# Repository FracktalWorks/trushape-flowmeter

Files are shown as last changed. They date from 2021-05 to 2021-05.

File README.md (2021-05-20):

# Trueshape Oxymeter
An open source oxygen flowmeter alternative using CNC machining, off the shelf parts and 3D Printing to meet the demand of flowmeters in India

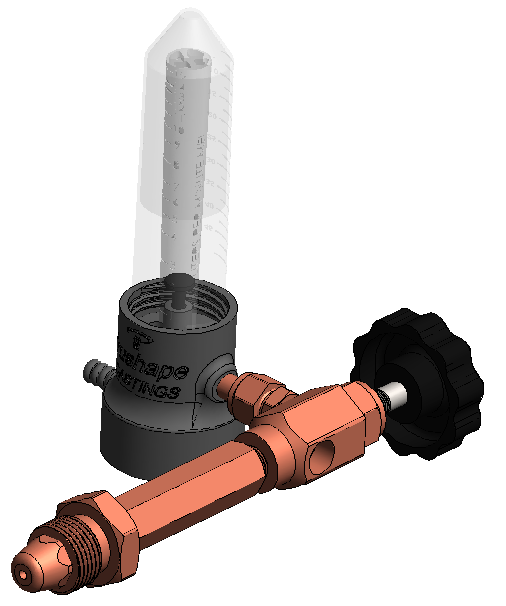
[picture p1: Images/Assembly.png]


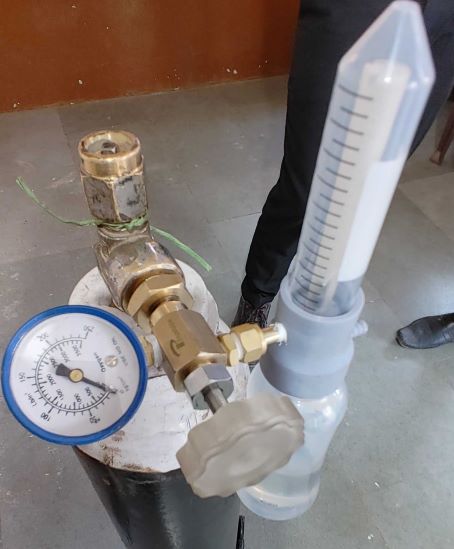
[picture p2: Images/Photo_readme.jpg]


### licence
------------------------------------------------------------------------------                                                
                                                                              
This source describes Open Hardware and is licensed under the CERN-OHL-S v2. 
                                                                              
You may redistribute and modify this source and make products using it under 
the terms of the CERN-OHL-S v2 (https://ohwr.org/cern_ohl_s_v2.txt).         
                                                                             
This source is distributed WITHOUT ANY EXPRESS OR IMPLIED WARRANTY,          
INCLUDING OF MERCHANTABILITY, SATISFACTORY QUALITY AND FITNESS FOR A         
PARTICULAR PURPOSE. Please see the CERN-OHL-S v2 for applicable conditions. 

As per CERN-OHL-S v2 section 4, should You produce hardware based on this source, You must where practicable maintain the Source Location visible      
on the external case of the Gizmo or other products you make using this
source.

------------------------------------------------------------------------------

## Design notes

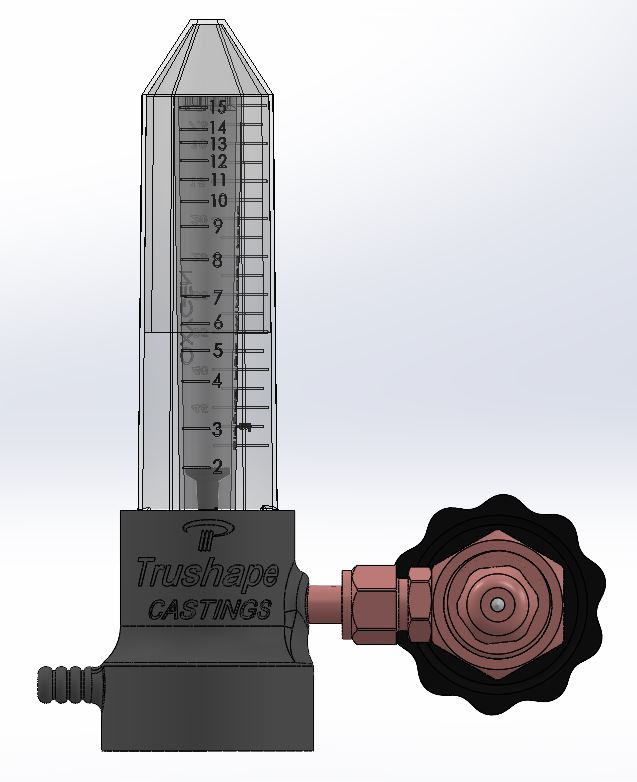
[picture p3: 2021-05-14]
Images/Front View.JPG

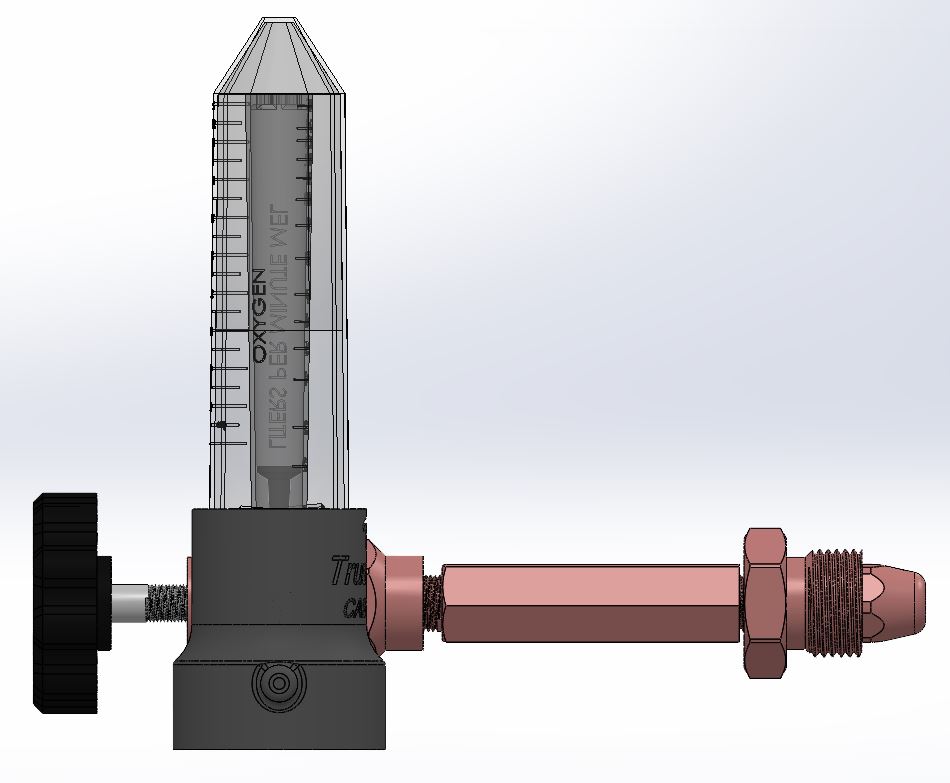
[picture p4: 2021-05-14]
Images/Side View.JPG

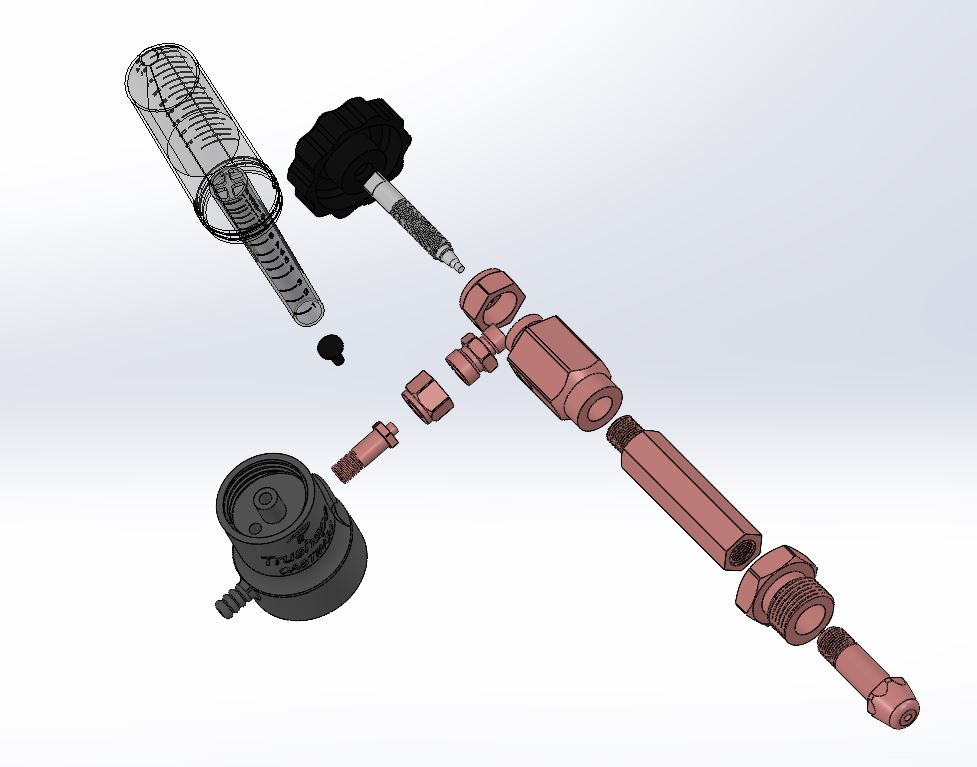
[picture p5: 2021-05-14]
Images/Exploded View.JPG

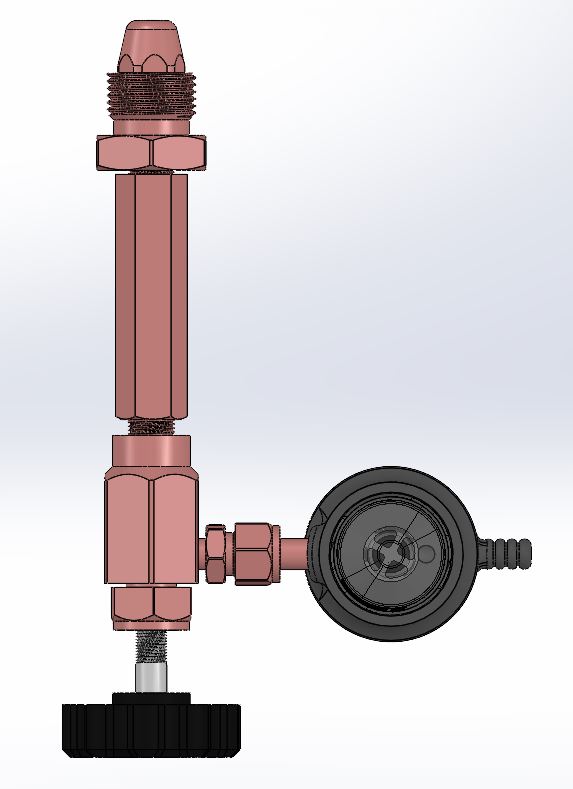
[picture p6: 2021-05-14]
Images/Top View.JPG

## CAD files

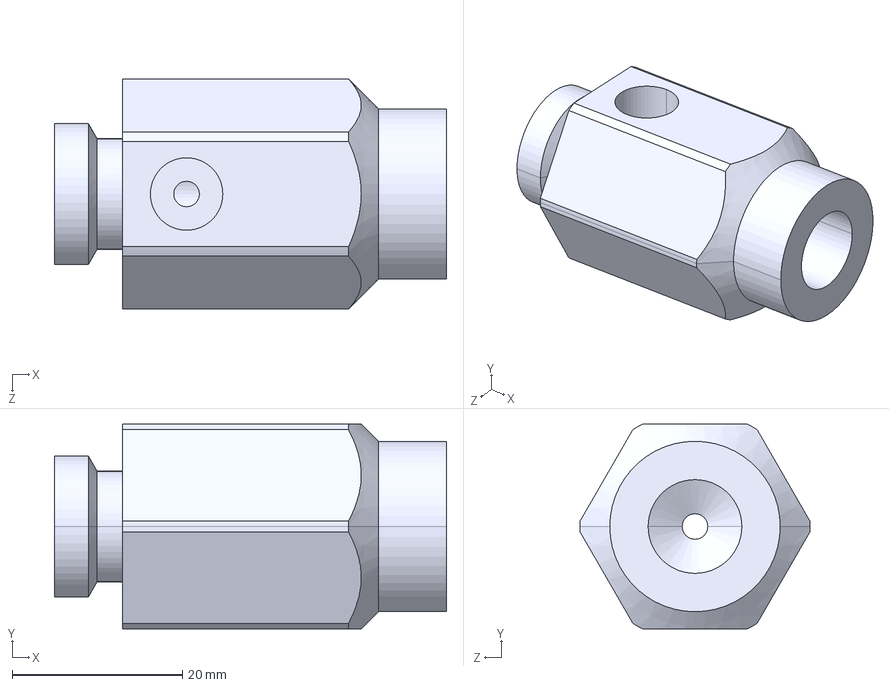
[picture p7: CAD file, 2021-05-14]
CAD Parts/Part6.STEP
46.0 x 24.0 x 27.0 mm

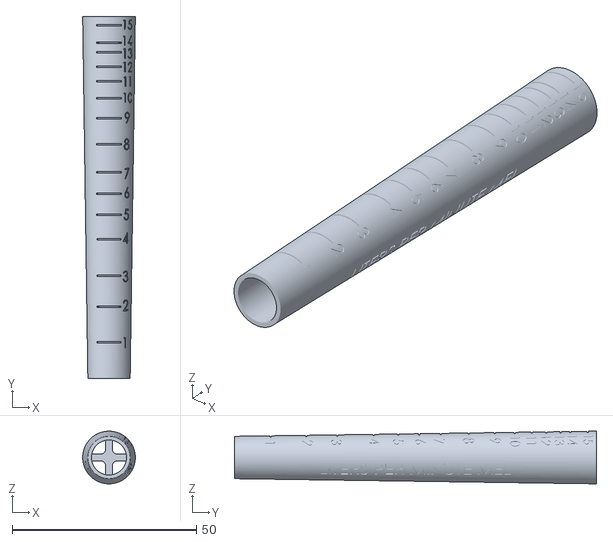
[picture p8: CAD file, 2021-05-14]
STL Files for 3D Printing/Inner Flow Gauge.STL
14.3 x 98.3 x 14.3

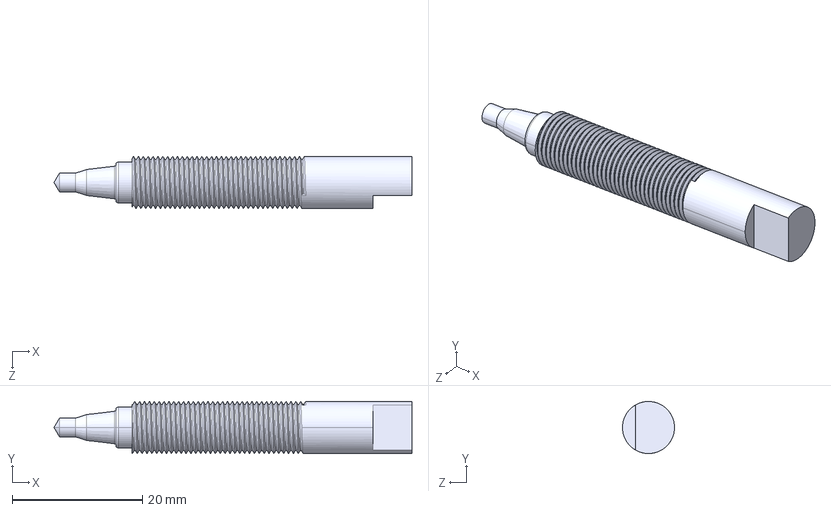
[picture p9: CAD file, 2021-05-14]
CAD Parts/Part1.STEP
55.0 x 8.00 x 8.00 mm

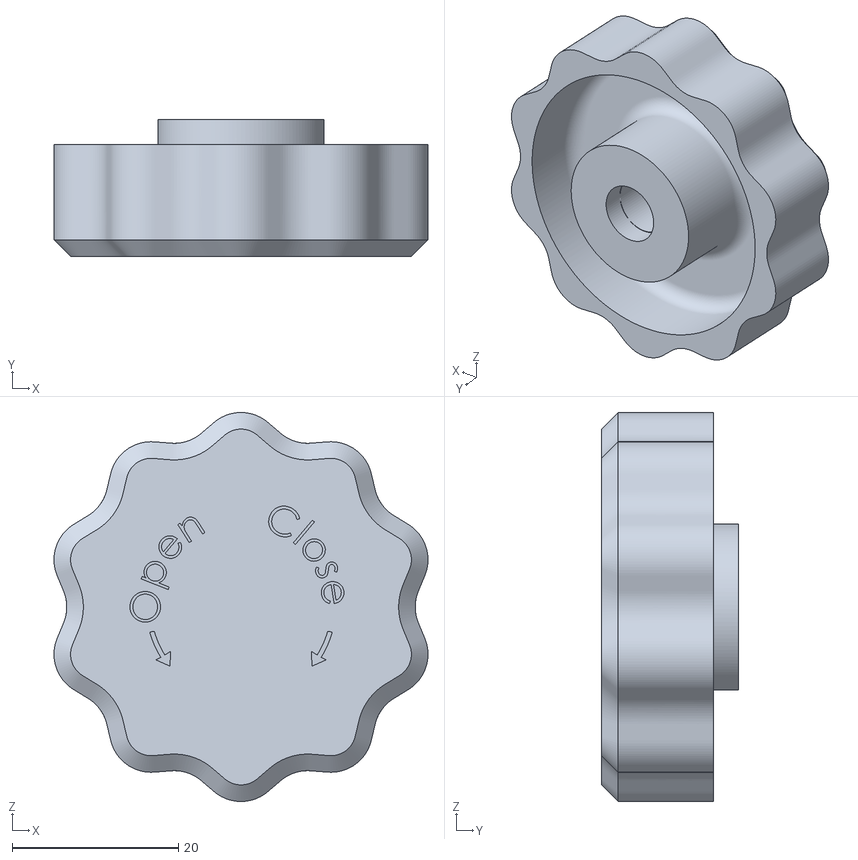
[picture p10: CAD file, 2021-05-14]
STL Files for 3D Printing/Part 1 Knob.STL
45.0 x 16.5 x 46.8

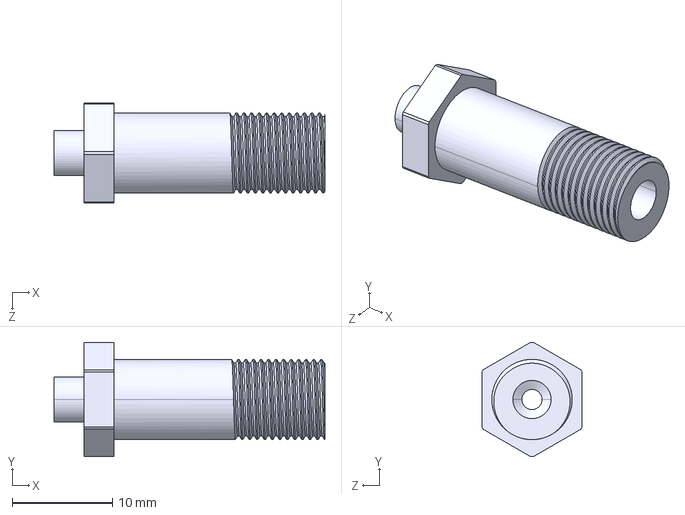
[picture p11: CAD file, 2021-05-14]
CAD Parts/Part7.STEP
27.0 x 11.4 x 10.0 mm

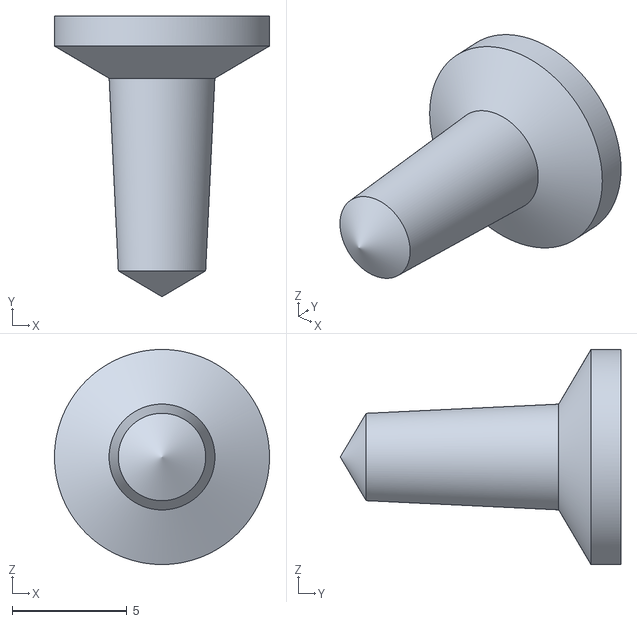
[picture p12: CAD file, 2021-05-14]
STL Files for 3D Printing/Indicator.STL
9.35 x 12.2 x 9.35

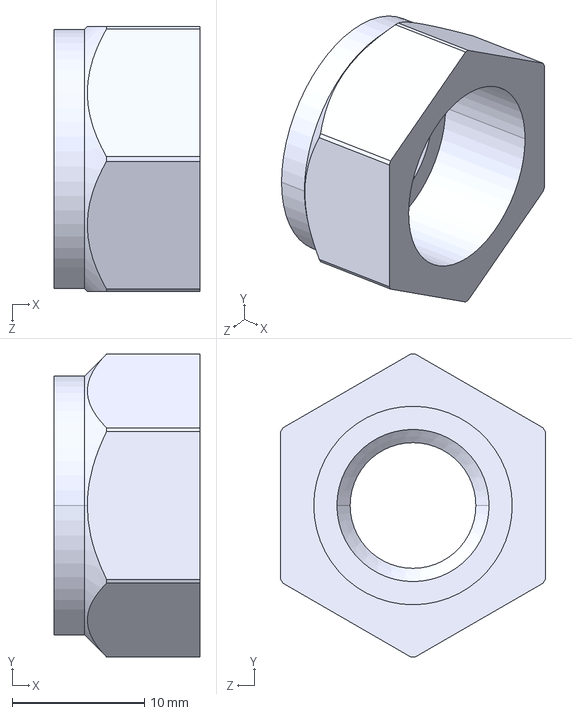
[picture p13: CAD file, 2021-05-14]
CAD Parts/Part9.STEP
11.0 x 22.9 x 20.0 mm

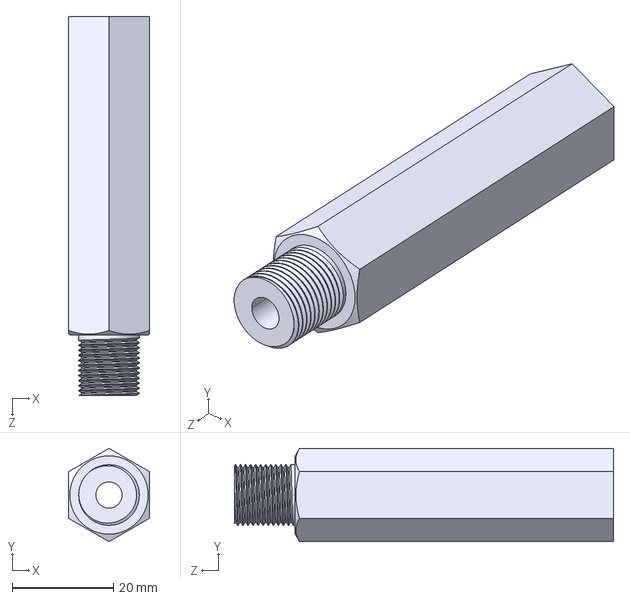
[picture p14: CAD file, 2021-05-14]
CAD Parts/Part12.STEP
16.0 x 18.5 x 75.0 mm

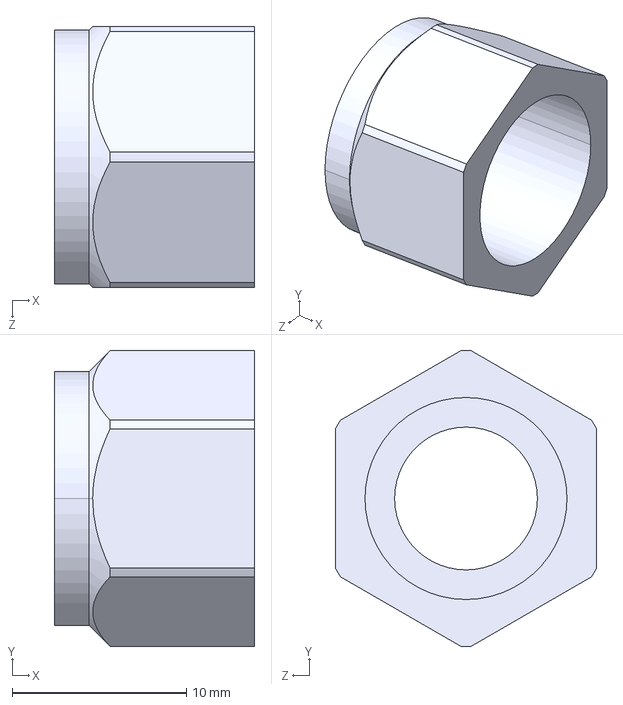
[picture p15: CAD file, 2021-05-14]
CAD Parts/Part11.STEP
11.5 x 17.0 x 15.0 mm

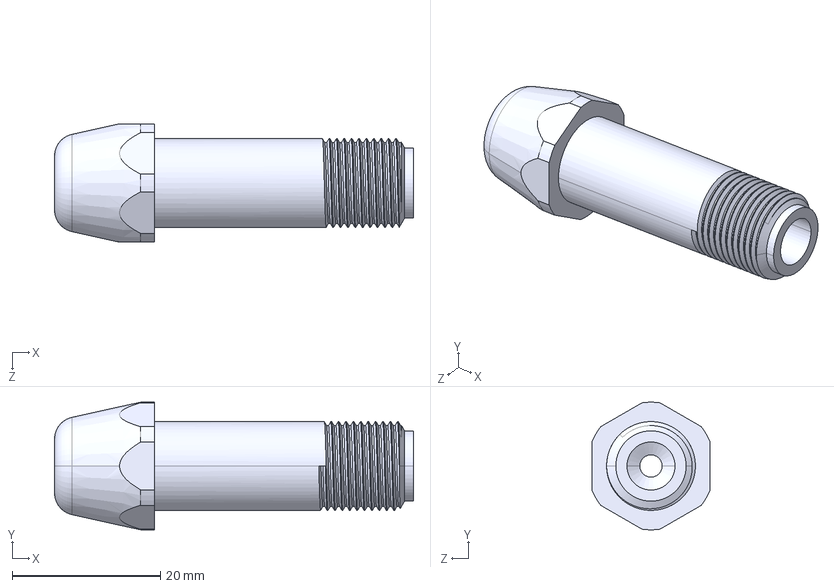
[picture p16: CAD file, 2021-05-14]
CAD Parts/Part5.STEP
48.5 x 17.2 x 16.0 mm

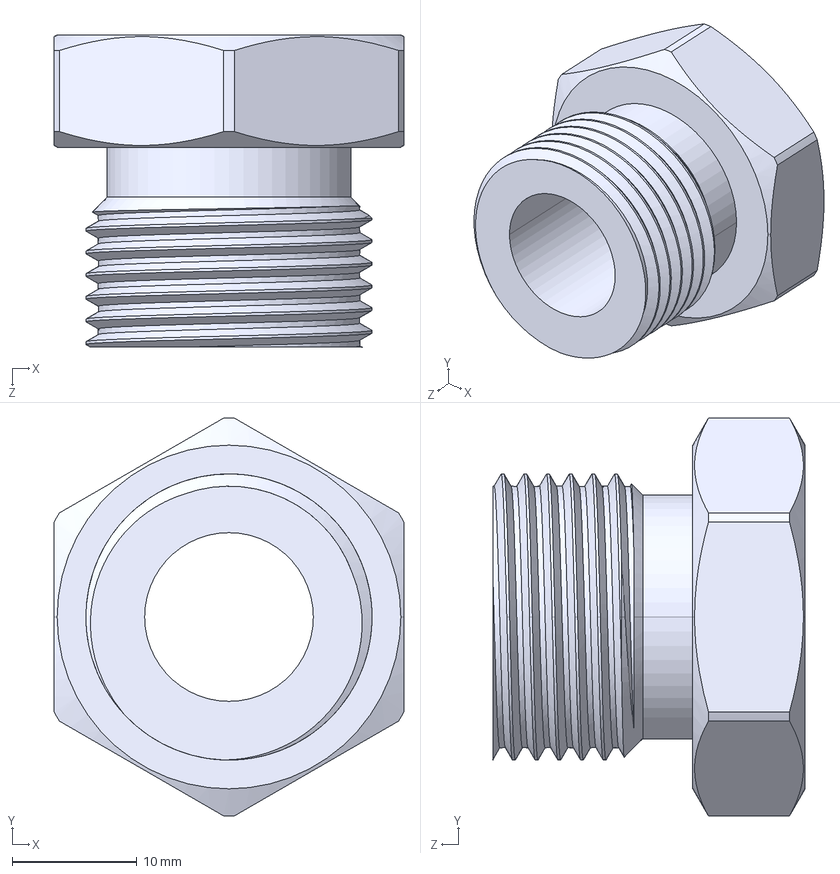
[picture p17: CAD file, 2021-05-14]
CAD Parts/Part8.STEP
28.0 x 31.8 x 25.0 mm

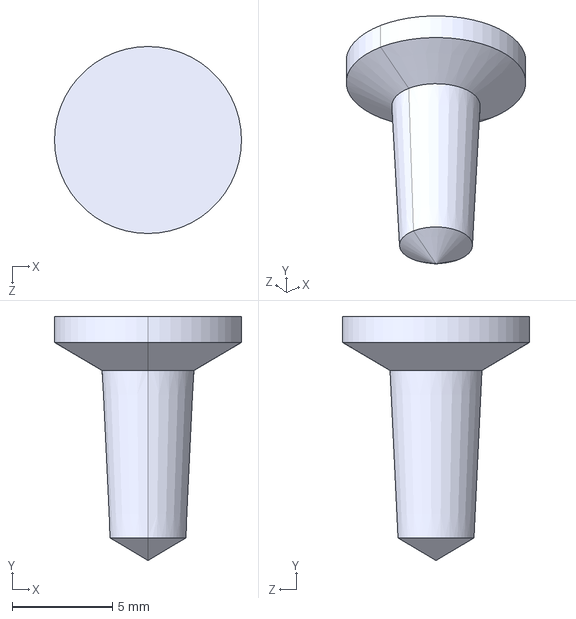
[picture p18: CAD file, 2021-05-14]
CAD Parts/Indicator.STEP
9.35 x 12.2 x 9.35 mm

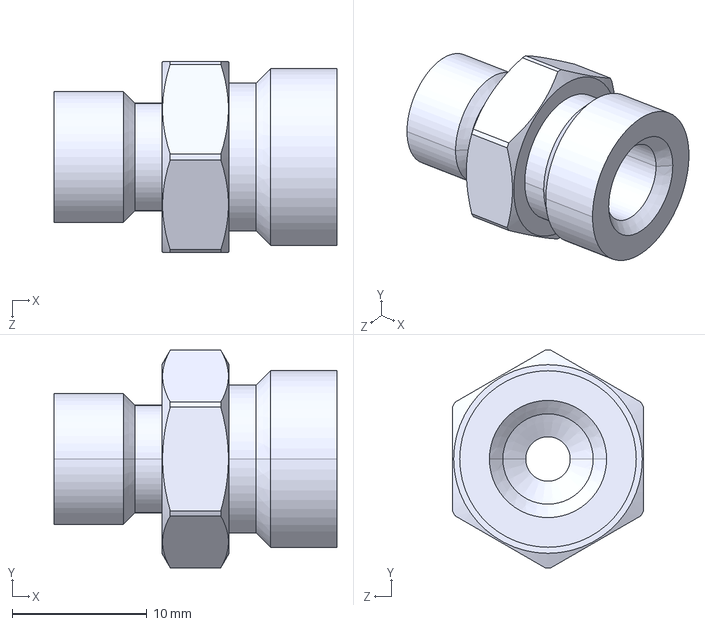
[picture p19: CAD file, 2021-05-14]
CAD Parts/Part10.STEP
21.0 x 16.1 x 14.2 mm

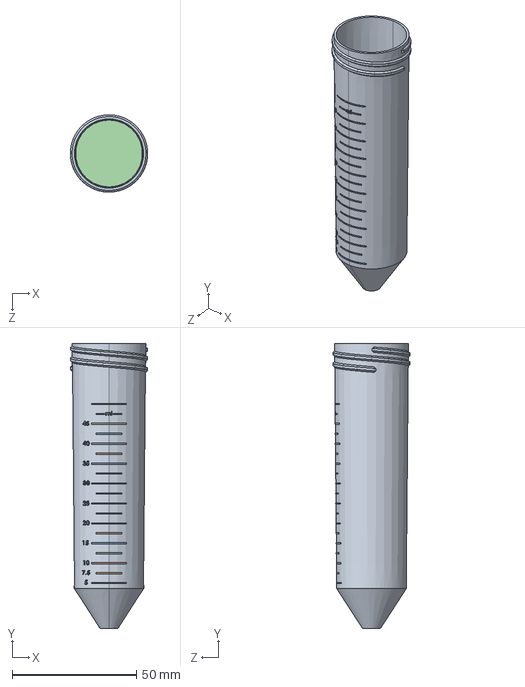
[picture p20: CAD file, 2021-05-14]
CAD Parts/50 ml Falcon tube Basic.STEP
31.1 x 114.6 x 31.1 mm

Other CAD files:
CAD Parts/Part 1 Knob.STEP

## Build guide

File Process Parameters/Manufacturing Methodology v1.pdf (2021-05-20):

Part No. as per CAD Model List | Image | Manufacturing Method | Material | Nomenclature | Company | Manufacturing Video Links | Important Remarks
Part00.STEP | | 3D Printing | Grey Resin | | | | Remove Supports properly and check each part by fitting the 50ml tube and bottle below. Use washers to prevent gas leakage.
Part9.STEP | | Readymade | Brass | Brass Nut 3/8
Part8.STEP | | CNC + Manual | Brass
Part7.STEP | | CNC + Manual | Brass
Part6.STEP | | CNC + Manual | Brass
Part5.STEP | | CNC + Manual | Brass
Part12.STEP | | CNC + Manual | Brass
Part11.STEP | | Readymade | Brass | Brass Nut 1/4
Part10.STEP | | Readymade | Brass | Brass Nipple 1/8 X 1/4
Part1.STEP | | CNC + Manual | Stainless Steel
Part1 Knob.STEP | | Readymade | Aluminium | | | | We 3D printed this first, were able to procure aluminium knobs hence aluminium is surely reliable than 3d printed sla part.
Inner Flow Gauge.STEP | | 3D Printing | Transparent Resin | | | | Give a thorough wash in IPA then cure and use an acrylic aerosol spray to coat the outer surface to obtain some level of transparency.

Trushape Flow Meter Manufacturing Methodology

Indicator.STEP | 3D Printing | Black Resin | | This printed part should be of 0.29 Grams (±0.01 Gms). You can sand out the head using a sand paper a little to maintain the weight
50ml Falcon Tube Basic.STEP | Readymade | Plastic | | Any 50ml centrifuge tubes used in laboratory would work. If possible etch the outer marking using MEK solution so that the doctor dosen't have any issue with reading the inner gauge L/min readings
Plastic Bottle (250ml) | Readymade | Plastic | MeeandMoms 250 ml Plastic Bottle | contact: ankur.agarwal@menmoms.co.in

Give reference: Faisal Kapasi from Trushape Precision Castings Pvt. Ltd.

Flex Tube | 8mm silicone tube | Readymade | Silicone
Pressure Gauge (200bar) (No Oil) | | Readymade | Brass/Stainless Steel | These needs to be procured from third party source

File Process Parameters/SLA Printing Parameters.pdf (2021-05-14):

Part Number | Name | Resin Used | Printer Used | Layer Height | Bottom Layer Count | Exposure Time | Bottom Exposure Time | Light-off Delay | Bottom Light-off Delay | Bottom Lift distance (mm) | Lifting Distance (mm) | Bottom Lift Speed (mm/min) | Lifting Speed (mm/min) | Retract Speed (mm/min)
Part 1.1 | Knob | Anycubic Black Resin | Elegoo Saturn | 0.05 | 8 | 1.5 | 50 | 0.5 | 0.5 | 6 | 6 | 180 | 180 | 240
Part 2 | Oxymeter | Anycubic Grey Resin | Anycubic Mono X and Elegoo Saturn | 0.05 | 8 | 1.5 | 50 | 0.5 | 0.5 | 6 | 6 | 180 | 180 | 240
Part 3 | Inner Flow Gauge | Anycubic Clear Resin | Anycibic Mono X | 0.05 | 8 | 2 | 50 | 0.5 | 0.5 | 6 | 6 | 180 | 180 | 240
Part 4 | Indicator | Anycubic Black Resin | Elegoo Saturn | 0.05 | 8 | 1.5 | 50 | 0.5 | 0.5 | 6 | 6 | 180 | 180 | 240
By: | Faisal Kapasi
Email: | faisal@tpclcastings.com
Contact: | -9601266798

### 3D Printing Parameters

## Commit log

2021-05-14 Added all CAD files
    [50 ml Falcon tube Basic.STEP, Indicator.STEP, Indicator.STL, Inner Flow Gauge.STL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]
2021-05-14 added assembly image
2021-05-14 added photo of device
